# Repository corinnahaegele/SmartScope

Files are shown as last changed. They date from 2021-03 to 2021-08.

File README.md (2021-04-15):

# SmartScope
Smartphone-attachable for low cost brightfield and fluorescence microscopic imaging

EAH-Jena-Logo_Schwarz

This Smartphone Microscope was constructed as a group project at the Ernst-Abbe-Hochschule Jena (University of Applied Sciences). The purpose of this project was to built a low-cost and high-resolution smartphone-attachable that is able to perform, both brightfield and fluorescence imaging. 
Since current benchtop microsopes usually are expensive, quite bulky and require a skilled operator, schools and developing countries often lack the access to high-resolution imaging devices. However most people posess a smartphone and the know-how to use the camera-apllication. Smartphones automatically save images in a digital file and by it's nature weigh little and able to transfer data wirelessly.

### Contributers: Eckart Hesse, Prof. Dr. Burkhardt Fleck, Evelina Jussupov, Corinna Hägele, Prof. Dr. Iwan Schie

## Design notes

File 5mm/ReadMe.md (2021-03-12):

#5mm Setup

This folder contains all the constructions for the f=5mm Setup.

Using the 5mm-Lense, resolutions in brightfield-mode ranged between 3 - 4μm.

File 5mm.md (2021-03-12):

# 5mm Setup

This folder contains all the constructions required for the application of the 5mm-lens

## Brightfield
- Basis for Huawei Nova/ Basis for Huawei P30Pro
- Brightfield Sampleholder 

## Fluorescence
- Lid.SLDPRT fits every constuction
- selection of barrel and Base depend on selected filter

### 12.5mm Filter
- Basis for Huawei Nova (Huawei P30 Pro does NOT fit here)
- Barrell for slide with sampple

### 25mm Filter
- Basis for Huawei Nova/ Basis for Huawei P30Pro
- Barrell for slide with sampple

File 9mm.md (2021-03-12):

# 9mm Setup

This folder contains all the constructions required for the application of the 9mm-lens

## Brightfield
- Basis for Huawei Nova/ Basis for Huawei P30Pro
- Sampleholder 

## Fluorescence: BF parts can be applied for fluorescence, Filter can simply be inserted between slide and barrell 
- Basis for Huawei Nova/ Basis for Huawei P30Pro
- Sampleholder 
- Lid.SLDPRT

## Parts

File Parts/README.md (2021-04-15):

### Smartphones:

current smartphone adapters have been implemented for geometries of following devices:
- Huawei Nova 
- Huawei P30 Pro
- Universal adapters should be suitable for most smartphones. They can be used for all setup-geometries EXCEPT for fluorescence imaging with 12.5mm filter!

### Lenses:
Setups were constructed and printed for following lenses:
- 9mm diameter and 9mm focallength: https://www.edmundoptics.eu/p/90mm-dia-x-90mm-fl-uncoated-plano-convex-lens/5572/
- 5mm diameter and 5mm focallength: https://www.edmundoptics.eu/p/50mm-dia-x-50mm-fl-uncoated-plano-convex-lens/5709/

### colour filters:
flourescence imaging was implemented using following filters:
- 12.5mm diameter and cut-off wavelength of 580nm: https://www.edmundoptics.de/p/o-58-580nm-125mm-dia-longpass-filter/20574/
- 25mm diameter and cut-off wavelength of 590nm: https://www.thorlabs.com/thorproduct.cfm?partnumber=FGL590M



Source of the diagram: https://www.edmundoptics.de/p/o-58-580nm-125mm-dia-longpass-filter/20574/ (Tab "Technische Abbildungen")

### LED:
excitation of fluorescent sample was achieved by using following LED:
- typical wavelenght 525nm: https://www.leds-and-more.de/catalog/smd-5050-plcc6-led-ultrahell-gruen-2500mcd-120-chip-p-1379.html?osCsid=tl46casp77ge3mi5qtluc61te4#!tab2

### Sample:
As fluorescent sample, red polyethylene microspheres were used. The beads can be excited by a broad spectrum of light and emitts red light with wavelength= 607nm
https://www.cospheric.com/UVPMSBR_fluorescent_red_spheres_density1090.htm.



Source of the images is: https://www.cospheric.com/UVPMSBR_fluorescent_red_spheres_density1090.htm

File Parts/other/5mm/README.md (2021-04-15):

# 5mm Setup

This folder contains all the constructions required for the application of the 5mm-lens.

## Brightfield
- Basis for Huawei Nova/ Basis for Huawei P30 Pro
- Brightfield sampleholder 

## Fluorescence
- Lid.SLDPRT fits every constuction
- selection of barrel and basis depend on selected filter

### 12.5mm Filter
- Basis for Huawei Nova (Huawei P30 Pro does NOT fit here)
- Barrel for slide with sample

### 25mm Filter
- Basis for Huawei Nova/ basis for Huawei P30 Pro
- Barrel for the slide with sample

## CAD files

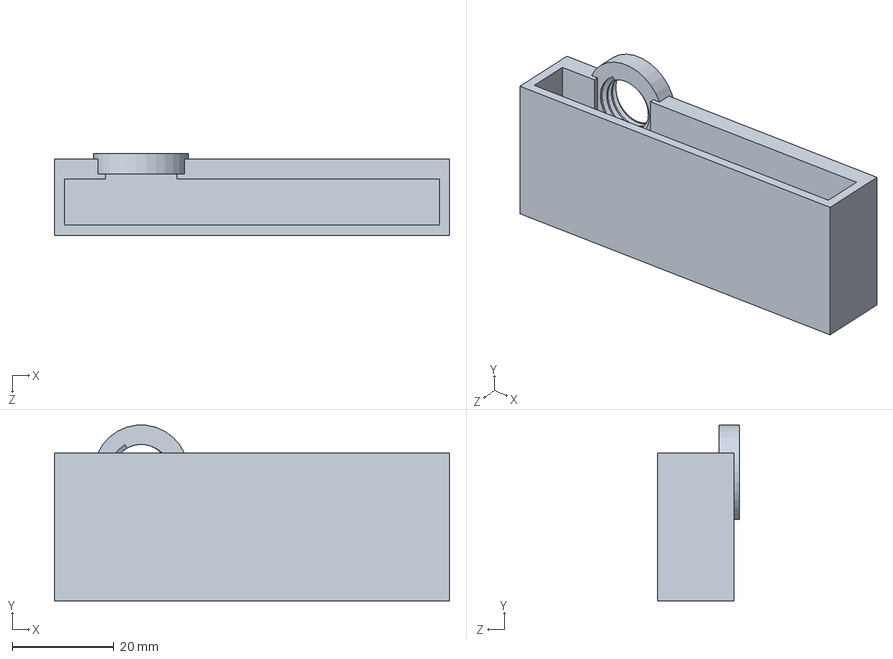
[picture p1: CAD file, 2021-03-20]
Parts/Basis/Basis_HuaweiP30Pro.SLDPRT
77.5 x 34.4 x 16.0 mm

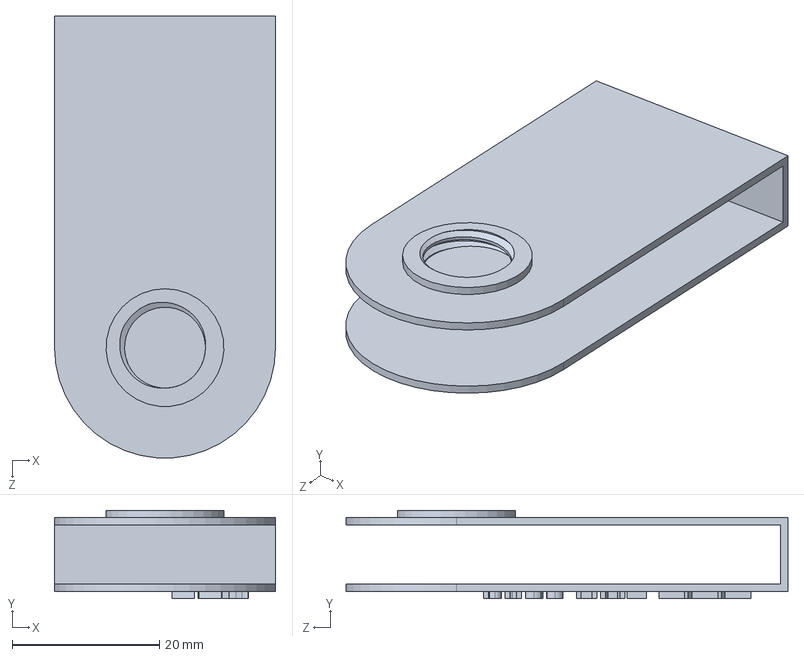
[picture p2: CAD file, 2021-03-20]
Parts/Basis/Universal Adapter/Klammer.SLDPRT
30.0 x 12.0 x 60.0 mm

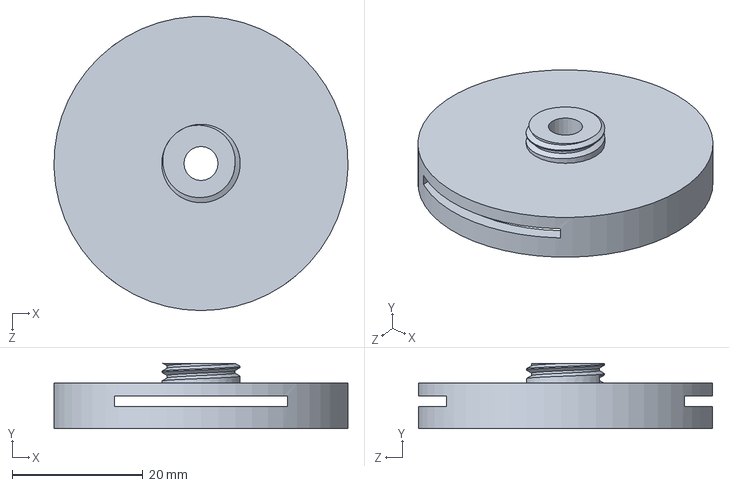
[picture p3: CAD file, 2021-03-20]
Parts/other/5mm/Brightfield/BF_Sampleholder.SLDPRT
45.0 x 10.0 x 45.0 mm

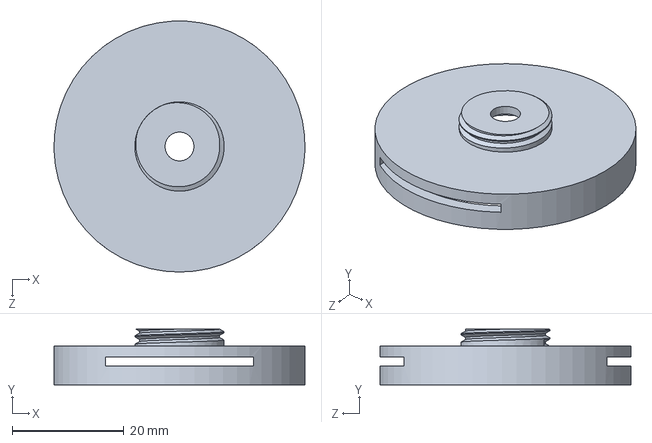
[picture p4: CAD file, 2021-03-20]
Parts/other/5mm/Fluorescence/12.5mm Filter/FL_Barrel_12.5mmFilter.SLDPRT
45.0 x 10.0 x 45.0 mm

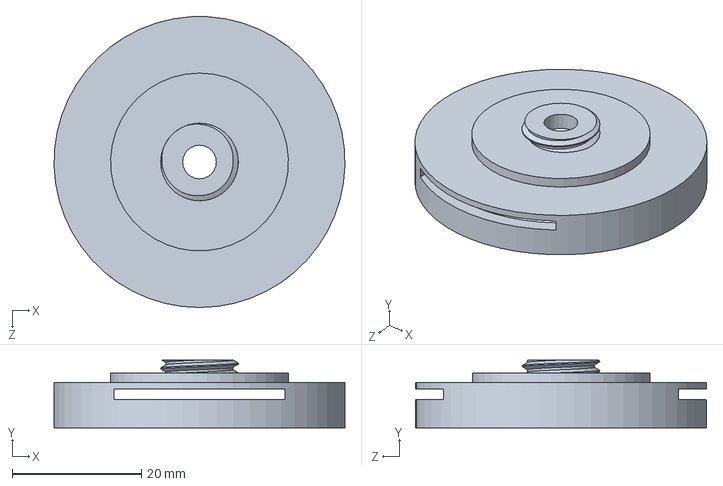
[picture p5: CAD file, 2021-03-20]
Parts/other/5mm/Fluorescence/25mm Filter/FL_Barrell_5mmLens_25mmFilter.SLDPRT
45.0 x 10.5 x 45.0 mm

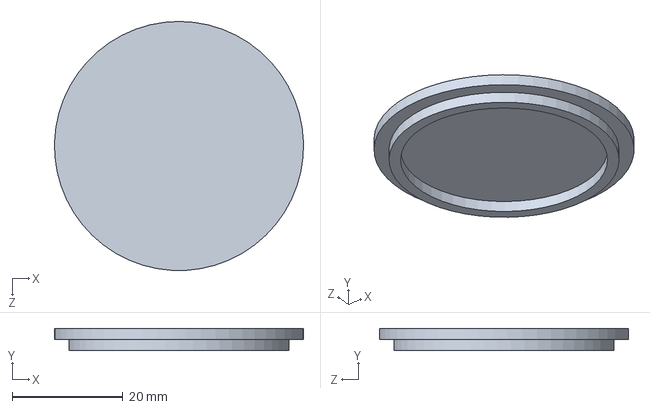
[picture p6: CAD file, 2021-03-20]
Parts/other/5mm/Fluorescence/FL_Lid.SLDPRT
45.0 x 4.00 x 45.0 mm

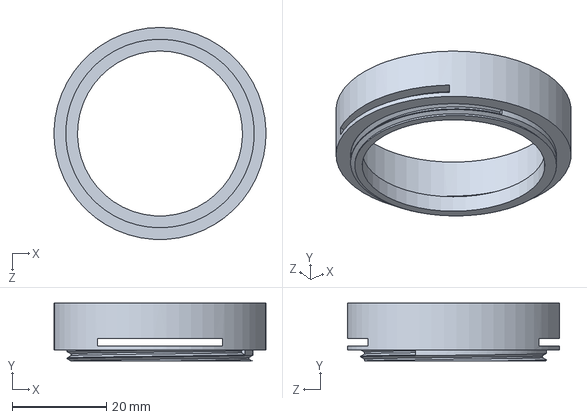
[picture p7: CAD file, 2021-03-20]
Parts/other/9mm/Sampleholder_9mmLens.SLDPRT
45.0 x 12.3 x 45.0 mm

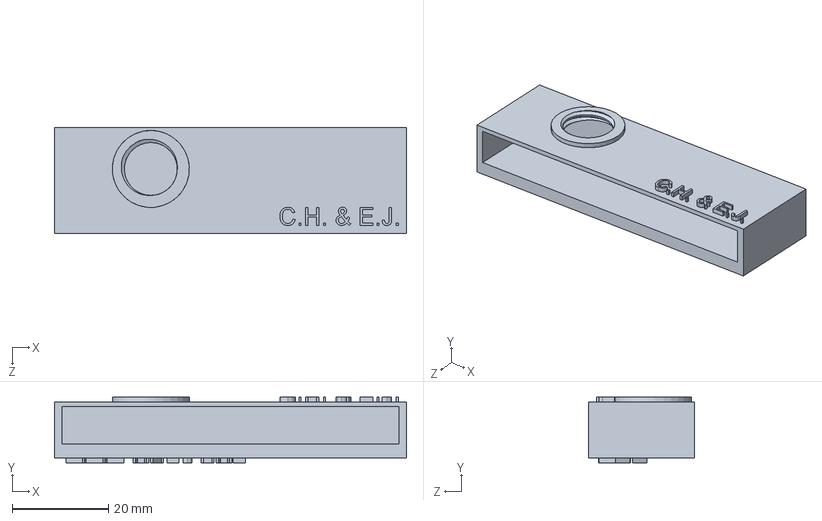
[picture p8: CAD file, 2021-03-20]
Parts/Basis/Basis_HuaweiNova.SLDPRT
73.1 x 13.7 x 22.0 mm

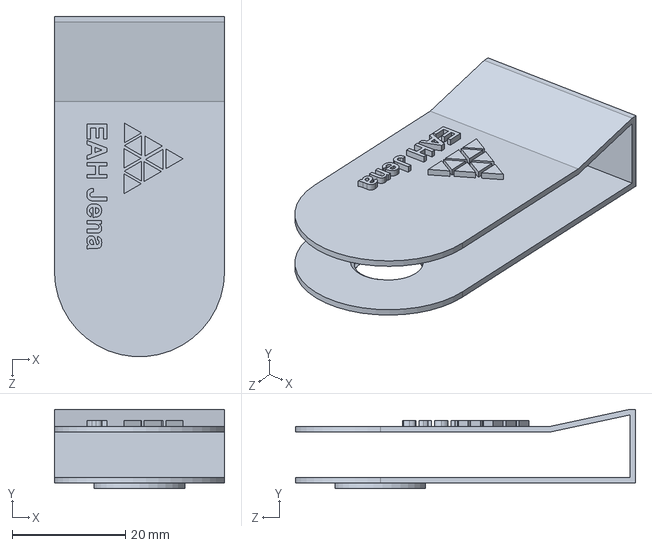
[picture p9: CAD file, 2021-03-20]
Parts/Basis/Universal Adapter/Klammer2.SLDPRT
30.0 x 14.0 x 60.0 mm

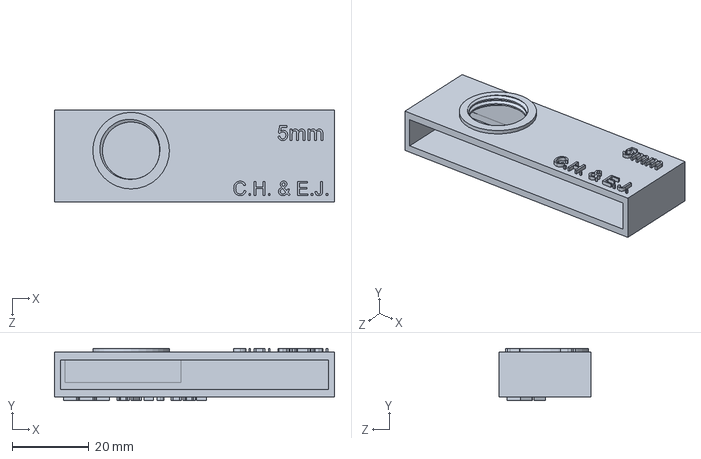
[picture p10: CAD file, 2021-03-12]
Parts/other/5mm/Fluorescence/12.5mm Filter/FL_Basis_HuaweiNova_12.5mmFilter.SLDPRT
73.1 x 13.7 x 24.0 mm

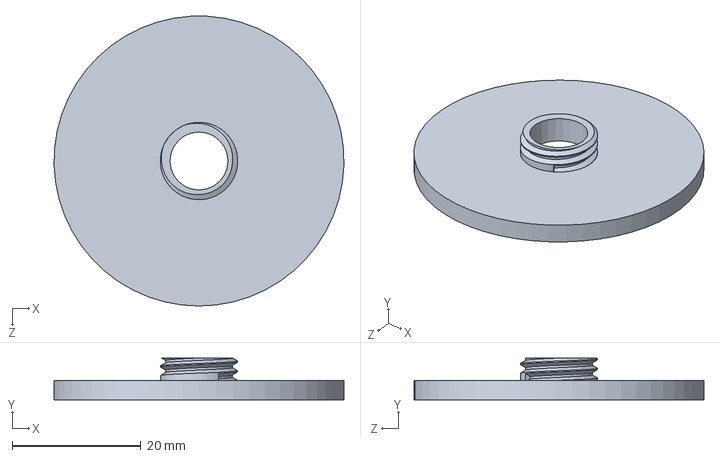
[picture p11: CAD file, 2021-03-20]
Parts/other/9mm/Barrell_9mmLens.SLDPRT
45.0 x 6.50 x 45.0 mm

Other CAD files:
Parts/other/9mm/Lid.SLDPRT

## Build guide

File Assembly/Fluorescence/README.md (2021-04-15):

# Instructions for assembly of fluorescence microscope

Choose the parts as listed in the folders 5mm or 9mm.
Follow the link for choosing the parts https://github.com/corinnahaegele/SmartScope/tree/main/Parts/other or go to SmartScope/Parts/other/.

Assemble the parts like shown in the pictures below:

## 9mm Setup
Insert the 9mm-lens in the barrell with the flat surface facing outwards. The surface of the lens should be flush with the barrell.

9mm_Insert_Lense

Insert the mobile phone into the basis-slot (display facing down) and mount the other parts (with lens inside of barrell). 
The color filter can be taped onto the barrel's inner surface so that it's center is above the lens.

9mm_fl

Lastly, insert the slide with the sample into the slot of the sampleholder.
The thread connecting sampleholder and barrell can be used to meet the exact focal lenght of the lens.

## 5mm Setup

Select whichever color filter you would like tu use and the corresponding sampleholder (Barrell and sampleholder are combined in ONE part) and basis-geometrie as listed. Insert the filter:
- 12.5mm Filter

12 5mm_filter

- 25mm Filter

25mm_filter

Insert the 5mm-lens in the sampleholder with the flat surface facing outwards. The surface of the lens should be flush with the sampleholder.

5mm_insert_lens

Insert the mobile phone into the basis-slot (display facing down) and mount the other parts (with lens inside of barrell)

5mm_Fl

Lastly, insert the slide with the sample into the slot of the sampleholder.

# Your smartphone microscope is now ready to take some images!

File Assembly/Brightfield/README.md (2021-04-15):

# Instructions for assembly of brightfield microscope

Choose the parts as listed in the folders 5mm or 9mm. 
Follow the link for choosing the parts https://github.com/corinnahaegele/SmartScope/tree/main/Parts/other or go to SmartScope/Parts/other/.

Assemble the parts like shown in the pictures below:

## 9mm Setup
Insert the 9mm-lens in the barrell with the flat surface facing outwards. The surface of the lens should be flush with the barrell.

9mm_Insert_Lense

Insert the mobile phone into the basis-slot (display facing down) and mount the other parts (with lens inside of barrell).

9mm_Assemble_Parts

Lastly, insert the slide with the sample into the slot of the sampleholder.
The thread connecting sampleholder and barrell can be used to meet the exact focal lenght of the lens.

## 5mm Setup
Insert the 5mm-lens in the sampleholder (Barrell and sampleholder are combined in ONE part) with the flat surface facing outwards. The surface of the lens should be flush with the sampleholder.

5mm_insert_lens

Insert the mobile phone into the basis-slot (display facing down) and mount the other parts (with lens inside of barrell)

5mm_BF

Lastly, insert the slide with the sample into the slot of the sampleholder.

# Your smartphone microscope is now ready to take some images!

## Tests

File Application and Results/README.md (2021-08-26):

The assembled microscope looks like this:

<p align="center">
  
</p>

# Brightfield imaging

For brightfield imaging, insert the glass slide into the slit intended for the slide. 
The sample should be on the surface facing away from the camera. 

When using the 9mm-setup, the thread between barrel and sampleholder can be used to adjust the slide to the optimal focal lenght. 
The 5mm-setup does not feature this extra thread since barrel and sampleholder are combined in one part. 

For optimal imaging results, hold your microscope setup against an ambient light source (like a window or a lamp). This will increase contrast and images will be sharper.

In the following image the dimensions of one cell of the used green algae sample are shown. 

<p align="center">
  
</p>

Following images were obtained with the Huawei Nova:

<p align="center">
  
</p>

## Resolution of brightfield imaging

Following resolutions were achieved in brightfield imaging (Huawei Nova):

<p align="center">
  
</p>

Due to background noise the actual resolution determined with the raleigh criterium is expected to be better than what is shown in the table. 

# Fluorescence imaging

For fluorescence imaging, insert the glass slide into the slit intended for the slide. 
The sample should be on the surface facing away from the camera. 

When using the 9mm-setup, the thread between barrel and sampleholder can be used to adjust the slide to the optimal focal lenght. 
The 5mm-setup does not feature this extra thread since barrel and sampleholder are combined in one part. 

Please use a dimmed environment for the imaging progress, as less ambient light reduces the amount of scattered light and images will be sharper.

Hold your LED-circuit onto one side of the slide, so that the LED is centered on the surface as shown in the following pictures and schematics. LED-light will be guided by Total Internal Reflection. 

<p align="center">
  
</p>

Schematic from: Sung, Y., Campa, F., Shish, W.C.: Open-source do-it-yourself multi-color fluorescence smartphone microscopy, Biomedical Optics Express, Vol. 8, November 2017

<p align="center">
  
</p>

The sizes of the microspheres ranged from 32µm to 38µm, which was important for determining the resolution of fluorescence imaging.

Following images were obtained with the Huawei Nova:#

<p align="center">
  
</p>

Following images were obtained with the Huawei P30 Pro:

<p align="center">
  
</p>

## Resolution of fluorescence imaging

The microspheres had fixed sizes from 32µm to 38µm and therefore were used as object micrometer. Since the particular size of the observed one microsphere was unknown, resolutions for both the best case scenario (32µm sphere) and worst case scenario (38µm sphere) were calculated and are shown in the tables below.

Following resolutions were achieved in fluorescence imaging (Huawei Nova):

<p align="center">
  
</p>

Following resolutions were achieved in fluorescence imaging (Huwei P30 Pro):

<p align="center">
  
</p>

The method used for the calculation was the method of "doubled lenght of pixels". The following picture shows the determination of pixel lenght with the software "imageJ" (here it is for best case scenario).

<p align="center">
  
</p>

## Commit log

2021-03-12 Update and rename 9mm_Lense to 9mm/README.md
2021-03-12 Update and rename Instructions/Brightfield to Assembly/Brightfield
2021-03-20 Stand 20.03.2021 Signed-off-by: cohae <cohae97@yahoo.de>
2021-03-20 Stand 20.03.2021
    [BF_NOVA_Basis_5mmLens.SLDPRT, BF_Sampleholder.SLDPRT, Barrell_9mmLens.SLDPRT, Basis_HuaweiNova.SLDPRT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]
